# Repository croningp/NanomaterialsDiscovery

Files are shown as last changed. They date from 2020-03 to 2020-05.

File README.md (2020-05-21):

# Nanomaterials Discovery

Software for the paper "A Nanomaterials Discovery Robot for the Darwinian Evolution of Shape Programmable Gold Nanoparticles" as published in Nature Communications.



# Software Requirements

This software requires the following:
* Python >= 3.6 ([Linux](http://docs.python-guide.org/en/latest/starting/install3/linux/) / [Windows](https://www.python.org/downloads/release/python-363/))
* [Arduino IDE](https://www.arduino.cc/en/Main/Software)
* [Arduino Command Handler](https://github.com/croningp/Arduino-CommandHandler)
* [Arduino Command Tools](https://github.com/croningp/Arduino-CommandTools)

## Python Libraries

To install all rquired Python libraries, run the following command: `pip install -r requirements.txt`

# Running The System

Information on firmware setup can be found [here](#arduino-firmware-setup)

The majority of the execution paramters for this platform are all defined in the platform's [`info.json`](nanobot_run/info.json) file. This defined how many generations of experiments to perform as well as which pumps to use, what parameters to use for the GA etc.

## Initial Start
* Make appropriate changes to the `info.json` file
* Navigate to `nanobot_analysis`
* Run the `heimddall.py` file
  * This will create the appropriate folders and populate them depending on algorithm type
  * Leave this window running if using `GA` mode

## Execution
* Navigate to `nanobot_run`
* Run either the `experiment.py` or `ga_experiment.py` file depending on your experiment mode
  * This will look in the appropriate filepaths set up by the `heimdall.py` script and begin to load and execute experiments
* Leave this to run and process experiments
  * `heimdall.py` will automatically process and store experimental data in the appropriate locations
  * This wil lalso update the GA algorithm with fitness values as the generations proceed.
* Once the generations are finished, the experiment has concluded.

# Arduino Firmware Setup

The following is a description of how to set up the Arduino firmware for use with Commanduino.

## Installation
Clone the following repositories and follow the basic set up instructions within (Works with Windows/Linux)
* [Arduino Command Handler](https://github.com/croningp/Arduino-CommandHandler)
* [Arduino Command Tools](https://github.com/croningp/Arduino-CommandTools)

## Basic Setup

* Include the Command Handler and Command Manager at the top of your file and create a CommandManager instance

```C++
#include <CommandHandler.h>
#include <CommandManager.h>
CommandManager cmdMgr;
```

* Include the basic Arduino devices you will be using e.g. AccelSteppers, Servos, etc.

```C++
#include <AccelStepper.h>
#include <LinearAccelStepperActuator.h>

/* Additional Modules if necessary */
```

* Next, include the "Command" version of all your included devices from above

```C++
#include <CommandAccelStepper.h>
#include <CommandLinearAccelStepperActuator.h>
```

* Now instantiate the Arduino device objects and their Command equivalents
    * Note: The numbers are pins and these may change depending on your setup  

```C++
AccelStepper stepper1(AccelStepper::DRIVER, 54, 55);
CommandLinearAccelStepperActuator cmdStepper(stepper1, 3, 38);

/* Additional Object creation */
```

## Setup Function

Within the setup function, we use the created CommandDevice objects and add them to the manager. Each object is given a unique ID that the user specifies.

```C++
void setup() {
    /* Here, "drive_wheel" is the unique ID */
    cmdStepper.registerToCommandManager(cmdMgr, "drive_wheel");

    /* Register the remaining devices in a similar fashion */
}
```

## Loop Function

The loop function only contains single call for the manager to update. Nothing else is required here.

```C++
void loop() {
    cmdMgr.update();
}
```

# Pin Mappings

One of the most common uses of Commanduino is controlling stepper motors for movement, pumps, etc. To be able to use multiple stepper motors on a single Arduino board, a RAMPS shield is used, giving access to 5 possible motor locations and a collection of pins for other devices. Below is a list of pin mappings for using multiple stepper motors on a single RAMPS shield.

```C++
X_STEP_PIN         54
X_DIR_PIN          55
X_ENABLE_PIN       38

Y_STEP_PIN         60
Y_DIR_PIN          61
Y_ENABLE_PIN       56

Z_STEP_PIN         46
Z_DIR_PIN          48
Z_ENABLE_PIN       62

E0_STEP_PIN         26
E0_DIR_PIN          28
E0_ENABLE_PIN       24

E1_STEP_PIN         36
E1_DIR_PIN          34
E1_ENABLE_PIN       30

X_MIN_PIN          3
X_MAX_PIN          2
Y_MIN_PIN          14
Y_MAX_PIN          15
Z_MIN_PIN          18
Z_MAX_PIN          19
```

# Commanduino Setup

This platform uses the COmmanduino library to facilitate all communication between the Arduino board and our Python interface.
More examples can be found [here](https://github.com/croningp/commanduino/tree/master/examples/commanddevices).

## Configuration File

Example config file:

```json
{
    "ios": [
        {
            "port": "/dev/ttyACM0"
        },
        {
            "port": "/dev/ttyACM1"
        },
        {
            "port": "/dev/ttyACM2"
        }
    ],
    "devices": {
        "wheel": {
            "command_id": "wheel",
            "config": {
                "reverted_switch": true,
                "revereted_driection": true,
                "enabled_acceleration": false,
                "speed": 12000,
                "homing_speed": 12000,
                "acceleration": 2000
            }
        },
        "module1": {
            "command_id": "modY",
            "config": {
                "add_whats_necessary_for_device": true
            }
        },
        ...

    }
}
```

### IOS

The ```ios``` key represents the USB port the Arduino port is connected to. Commanduino will scan these ports to find the appropriate Arduino attached. For a single arduino attached, the above setup for ```ios``` is sufficient but for multiple Arduinos, it is best to assign them to a single port only. This prevents clashes.  
For port names:

* Linux
    * `"/dev/ttyACM{number}"`
* Windows
    * `"COM{number}"`

### Devices

The ```devices``` key holds all the information for the devices attached to the Arduino board. In the example above, ```wheel``` and ```module1``` are the names Commanduino will use to access them. Inside the devices, we have the ```command_id``` and ```config```.
* ```command_id```
    * This is unique ID given in the Arduino file. (See [Arduino Setup](#arduino-setup))
* ```config```
    * Dependent on the device type. (See [Commanduino Device Examples](https://github.com/croningp/commanduino/tree/master/examples/commanddevices))

## Commanduino File

Example Commanduino file:

```python
import os
import sys
import json
import time
import inspect

from commanduino import CommandManager # <-- Important!

class CoreDevice(object):
    """
    Class representing a core Commanduino system.
    Allows access to the modules attached

    Args:
        config (str): path to the Commanduino config file
    """
    def __init__(self, config):
        self.mgr = CommandManager.from_configfile(config) # Creates the CommandManager with JSON configuration file

        # Can now access devices attached e.g.
        self.wheel = self.mgr.wheel
        self.module1 = self.mgr.module1
        # etc. etc.

    ...

```

# Authors

* Daniel Salley
* Graham Keenan
* Abhishek Sharma
* Jonathan Grizou
* Sergio Martin Marti
* Leroy Cronin

All software and designs were developed as members of the [Cronin Group (University of Glasgow)](http://www.chem.gla.ac.uk/cronin/)

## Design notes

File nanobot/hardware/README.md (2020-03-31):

# NanoBot_hardware_V1
This repository contains all of the STL and DXF files and commercial component links needed to build an original 15 slot NanoBot platform

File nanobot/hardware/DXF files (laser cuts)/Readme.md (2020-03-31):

# DXF for laser cutting

The DXF file here contains the four laser cut acrylic parts (4mm) needed for the platform:
* The vial tray top and bottom
* The base plate
* The stirring ring on which the fans are mounted

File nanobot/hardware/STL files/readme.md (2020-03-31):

# Notes of these parts:

* These components have been designed for printing on an Objet series Connex 3D printer. This printer is extremely accurate meaning the allowances left between screw housings, part to part contact points etc. are in the order of microns. This means most (if not all) FDM print technology would be insufficient to print these parts as they currently stand. The structural parts (base and column etc) with a sufficient quality FDM printer may work with some manual adjustment after printing. However the drive and drive wheel relations are where the main issues will arise. This problem can be accounted for by the following steps:
  - Using the following links to [Geneva wheel basics](https://newgottland.com/2012/01/08/make-geneva-wheels-of-any-size/) and a [Genever wheel calculator](http://benbrandt22.github.io/genevaGen/) you may generate new dimensions needed for a fresh design with allowances sufficient for FDM printing.
  - Using the dimensions for the drive and drive wheel overall sizes provided in the DXF file included in this repo a replacement could be produced.

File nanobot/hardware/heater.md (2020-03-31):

## controller

- https://www.amazon.co.uk/Inkbird-Temperature-Controller-Thermostat-Thermocouple/dp/B00ADEGW3C/ref=sr_1_1?ie=UTF8&qid=1468329202&sr=8-1&keywords=ITC-100RL

## sensors

- http://uk.rs-online.com/web/p/thermocouples/8722503/

## heater

- http://incubatorwarehouse.com/incukit-xl.html

- heater from this company to heat the chamber: http://kuehlingkuehling.de/product-category/3d-printers/

## various

- http://uk.rs-online.com/web/p/non-latching-relays/7826969/

- http://uk.rs-online.com/web/p/non-latching-relays/0351572/

- http://uk.rs-online.com/web/p/crimp-terminal-boots/7454794/

- http://uk.rs-online.com/web/p/crimp-receptacles/0534351/?origin=null|fp&cm_sp=featureproducts-_-FeaturedProductsContent-_-0534351

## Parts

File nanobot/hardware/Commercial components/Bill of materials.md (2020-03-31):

# Bill of Materials

This page contains a brief description of and links for the commercially available parts needed to produce this platform   

# Wheel platform

* Structural: V-slot aluminium [profile](http://ooznest.co.uk/V-Slot/Linear-Rails/V-Slot-Linear-Rail-2020mm):
  - 290mm x 2
  - 300mm x 2
  - 260mm x 1
  - 120mm x 2
  - 180mm x 1
* Structural: M5 x 12, 8 and 6mm [screws](http://ooznest.co.uk/Low-Profile-M5-Bolts?search=M5) with accompanying [drop-in tee nuts](http://ooznest.co.uk/Drop-In-Tee-Nuts?search=drop)
* Structural: Universal (single) L-[bracket](http://ooznest.co.uk/V-Slot/Brackets/Universal-L-Brackets)
* Structural: 2-hole [joining plate](http://ooznest.co.uk/V-Slot/Brackets/2-Hole-Joining-Plate) x 2
* Structural: [Acrylic](http://www.acrylic-online.co.uk/) sheet 4mm (600 x 500mm minimum) x 1
* Structural: Assorted 3D printed [parts](https://github.com/croningp/NanoBot_hardware_V1/tree/master/STL%20files)
* Structural: Assorted M3 x 12/16/20/30mm [screws](https://www.accu.co.uk/en/64-low-head-cap-screws#elasticsearch_id_feature_655793=655793_697&elasticsearch_id_feature_655794=655794_1&id_elasticsearch_category=64&orderby=ranking&orderway=asc)
* Electronic: Arduino mega 2560 and [RAMPS](http://ooznest.co.uk/RAMPS-14-Controller-Board-Premium?search=ramps) 1.4 with 2 DRV8825. The options for the Arduino and stepper motor drivers are included in the drop down menu options x 1
* Electronic: 25 x 25 x 10 mm DC [fans](http://ooznest.co.uk/12V-DC-25mm-Fan?search=25mm) for the stirring array x 15
* Electronic: Corsair SF450 [power supply](https://www.amazon.co.uk/Corsair-SF450-Fully-Modular-Supply/dp/B01CR5XJR6) x 1
* Electronic: Nema17 stepper x 1 [motor](https://www.accu.co.uk/en/nema-17-stepper-motors/496466-NEMA17-40-1-7-1-8?uk_google_shopping=1&c=3&mkwid=s_dc&pcrid=209417175255&kword=&match=&plid=&gclid=CjwKCAjwyrvaBRACEiwAcyuzRABbU2tFQi1yQNd7_wL3WTq4IH_Au6toDr7JEU6PAY236qg2CjXwfBoCHX8QAvD_BwE) with accompanying Pololu aluminium mounting [hub](https://www.pololu.com/product/1998) (this part joins the drive wheel to the stepper motor shaft) x1
* Electronic: Any 2 and 4 way crimp housings. It matters that the crimps match the plastic housings you chose, beyond that many types can be used.
* Electronic: Stepper motor to RAMP connection [housings](https://uk.rs-online.com/web/p/products/2964956/?grossPrice=Y&cm_mmc=UK-PLA-DS3A-_-google-_-PLA_UK_EN_Connectors-_-Pcb_Connectors%7CPcb_Connector_Housings-_-PRODUCT+GROUP&matchtype=&gclid=CjwKCAjwyrvaBRACEiwAcyuzROPybPC5snwsWROQbjWMcLjBqjNpqaopkuRLn16-PZd7FsV7mNAtghoCZcMQAvD_BwE&gclsrc=aw.ds) x 1 per stepper motor (use with appropriate crimps for this housing)
* Electronic: End stop switch (modular syringe driver) crimp housings for RAMPS [connection](https://www.molex.com/molex/products/datasheet.jsp?part=active/0050579003_CRIMP_HOUSINGS.xml) (use with appropriate crimps for this housing)
* Pumps: Tricontinent [c-series pumps](https://www.tricontinent.com/c-series-syringe-pumps.html) x 8
* Pumps: Tubing and connectors from Kinesis/Cole-Palmer:
  - [1.6mm](https://kinesis.co.uk/tubing-tubing-ptfe-1-16-1-6mm-od-x-0-8mm-id-20m-008t16-080-20.html) OD tubing
  - [3.2mm](https://kinesis.co.uk/tubing-tubing-ptfe-1-8-3-2mm-od-x-1-5mm-id-10m-008t32-150-10.html) OD tubing
  - IDEX flangeless fittings Nat PP [1/16in](https://www.idex-hs.com/store/fluidics/fluidic-connections/fittings/flat-bottom-fittings/flangeless-fittings/flangeless-fitting-natural-polypropylene-1-4-28-flat-bottom-for-1-16-od.html)
  - IDEX flangeless fittings Nat PP [1/8](https://www.idex-hs.com/store/fluidics/fluidic-connections/fittings/flat-bottom-fittings/flangeless-fitting-natural-polypropylene-1-4-28-flat-bottom-for-1-8-od.html)
  - Restek Thames 1/4-28 female to male [Luer]() asy
  - Adhesive Dispensing (AD5125TLC) 25 gauge TLC lined tip [needle]()
* Fan stirring [magnets](https://www.first4magnets.com/rectangular-magnets-c35/15-x-4-x-4mm-thick-n42-neodymium-magnet-2-2kg-pull-p3499#ps_1-789) x 30
* Driven wheel [bearing](https://uk.rs-online.com/web/p/ball-bearings/4420082/) x 1
* Modular syringe [driver] (https://github.com/croningp/ModularSyringeDriver)

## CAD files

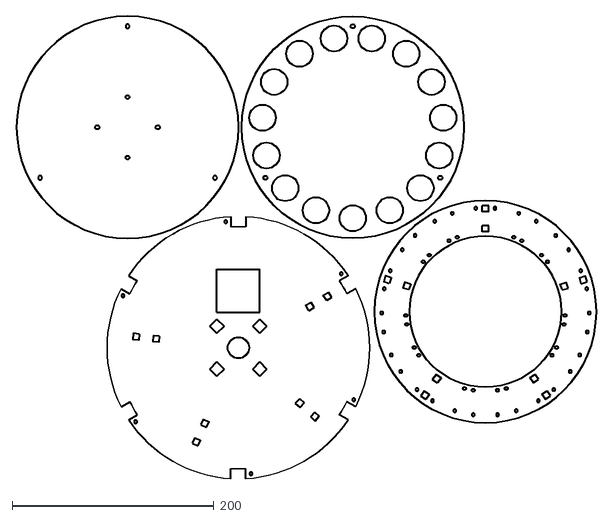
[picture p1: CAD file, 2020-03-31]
nanobot/hardware/DXF files (laser cuts)/NanoBot_cuts.dxf
574.4 x 458.0

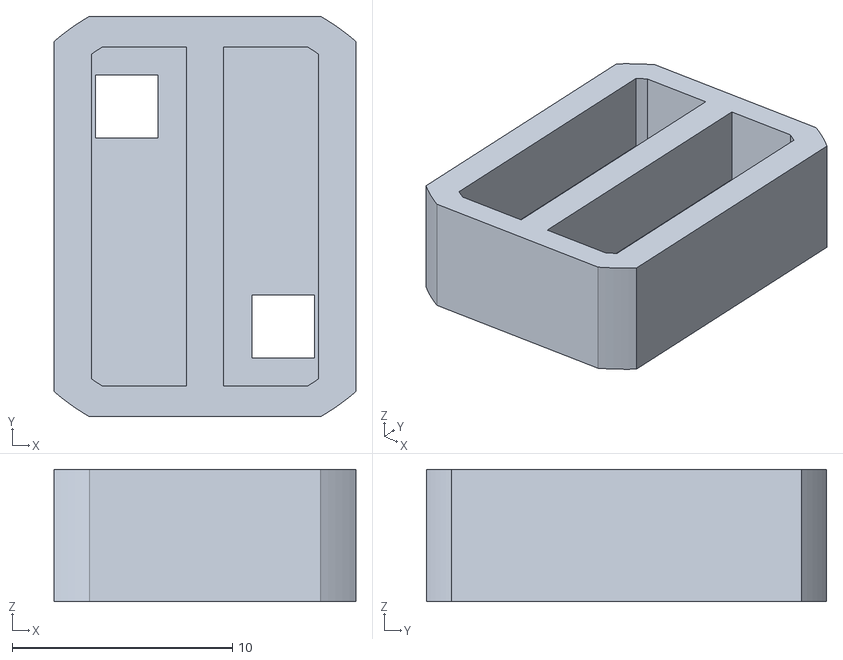
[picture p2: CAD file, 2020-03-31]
nanobot/hardware/STL files/NanoBot magnet housing 2.2kg pull rectangular.stl
13.7 x 18.2 x 6.00

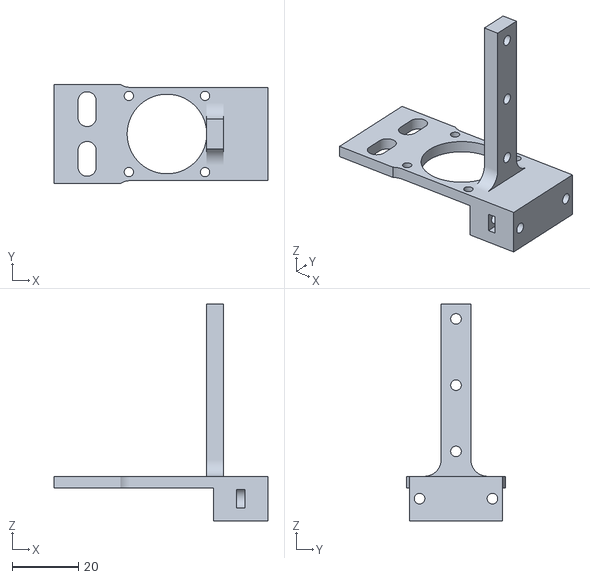
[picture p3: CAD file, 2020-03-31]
nanobot/hardware/STL files/Syringe driver prints/NanoBot syringe body.stl
64.6 x 30.0 x 65.5

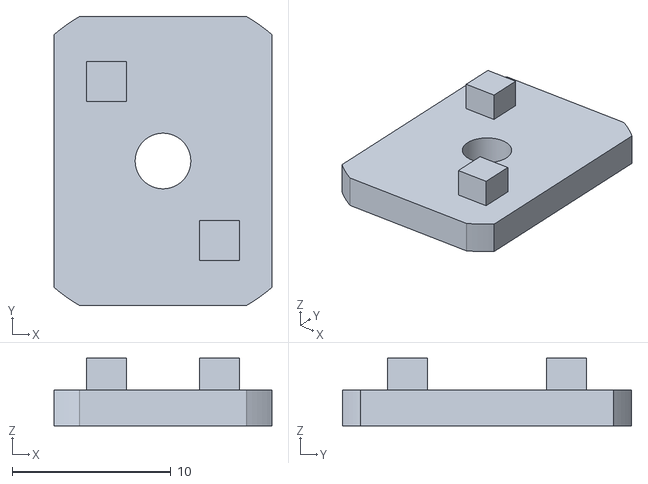
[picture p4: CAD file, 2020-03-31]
nanobot/hardware/STL files/NanoBot magnet housing base.stl
13.7 x 18.2 x 4.25

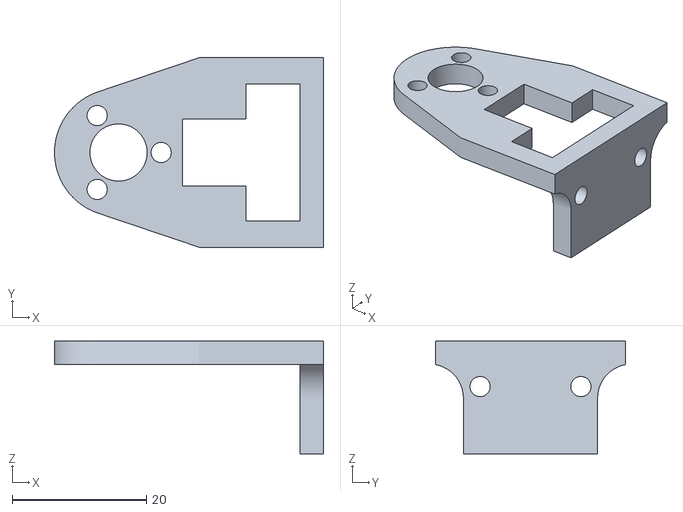
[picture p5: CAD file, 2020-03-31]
nanobot/hardware/STL files/Syringe driver prints/NanoBot syringe carriage body.stl
40.0 x 28.2 x 16.8

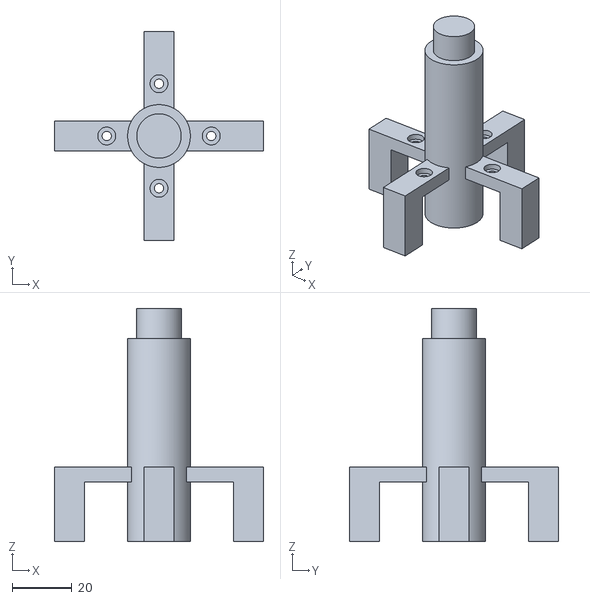
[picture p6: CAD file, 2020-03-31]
nanobot/hardware/STL files/NanoBot Column mount.stl
70.0 x 70.0 x 78.0

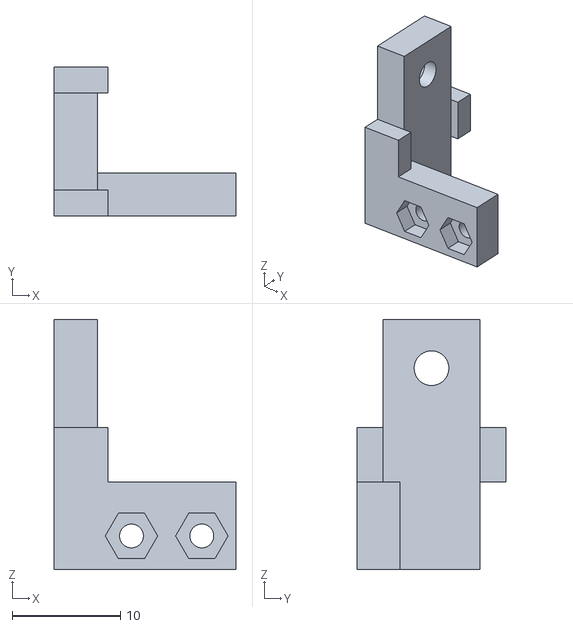
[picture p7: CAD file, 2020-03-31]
nanobot/hardware/STL files/Syringe driver prints/NanoBot syringe end stop switch mount.stl
16.8 x 13.8 x 23.1

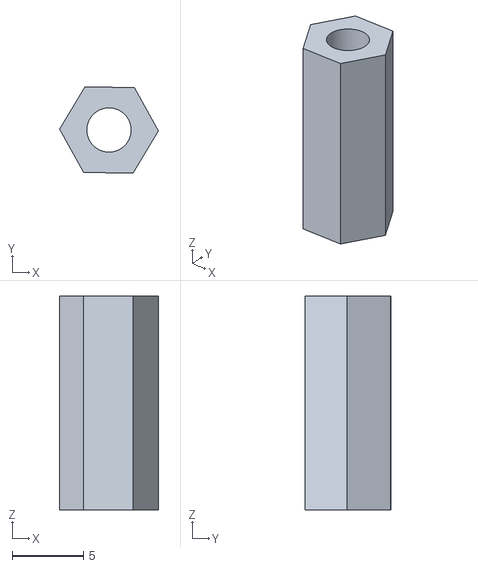
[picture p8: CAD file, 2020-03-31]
nanobot/hardware/STL files/NanoBot vial tray hex spacer.stl
6.93 x 6.06 x 15.0

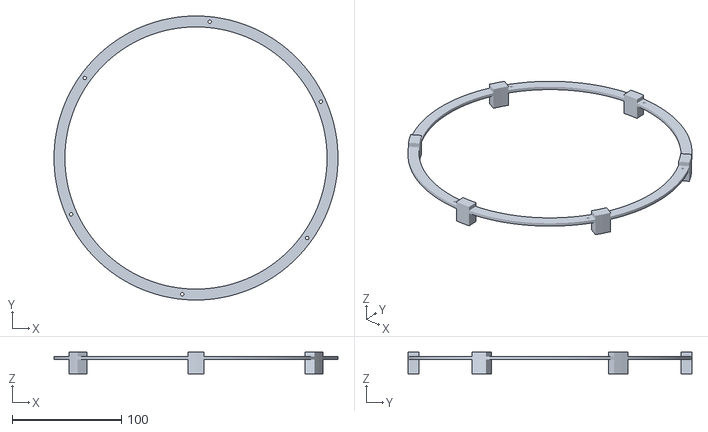
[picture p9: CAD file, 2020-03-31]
nanobot/hardware/STL files/NanoBot Base platform.stl
260.0 x 260.0 x 20.0

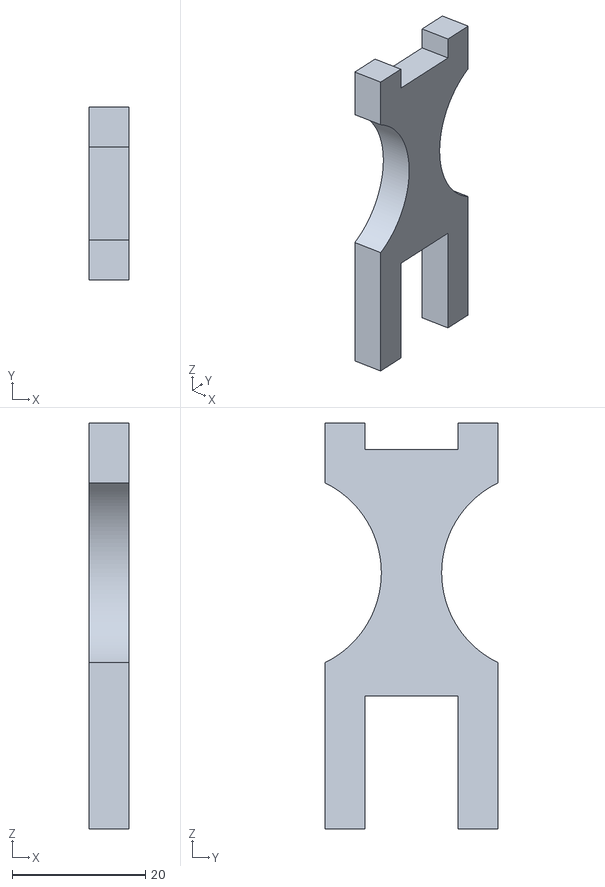
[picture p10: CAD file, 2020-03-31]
nanobot/hardware/STL files/NanoBot Stir ring support.stl
6.00 x 26.0 x 61.0

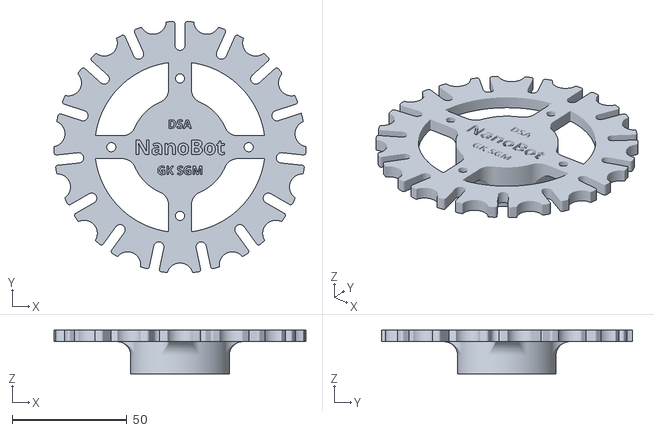
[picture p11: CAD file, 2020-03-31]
nanobot/hardware/STL files/NanoBot Driven wheel.stl
110.0 x 109.6 x 19.0

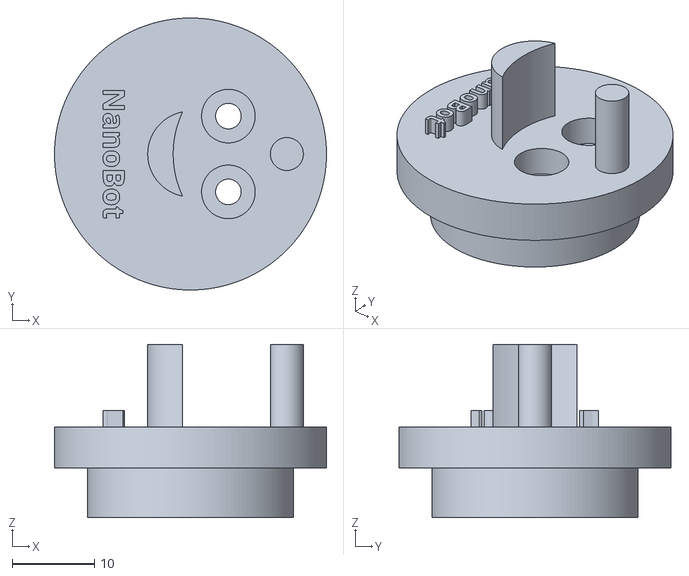
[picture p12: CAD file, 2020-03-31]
nanobot/hardware/STL files/NanoBot Drive wheel.stl
33.0 x 33.0 x 21.0

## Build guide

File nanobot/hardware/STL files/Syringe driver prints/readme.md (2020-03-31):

# Modular syringe driver:

This set of STL files are an in house design for a Modular syringe driver capable of Z-motion movement that allows us to lower probes, tubing etc. into our reaction vials.  
The links for the custom made stepper motor and the other commercial hardware needed to make this unit can be found in the 'commercial parts' folder

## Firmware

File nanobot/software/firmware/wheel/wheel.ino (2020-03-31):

/**
#define X_STEP_PIN         54
#define X_DIR_PIN          55
#define X_ENABLE_PIN       38

#define Y_STEP_PIN         60
#define Y_DIR_PIN          61
#define Y_ENABLE_PIN       56

#define Z_STEP_PIN         46
#define Z_DIR_PIN          48
#define Z_ENABLE_PIN       62

#define E0_STEP_PIN         26
#define E0_DIR_PIN          28
#define E0_ENABLE_PIN       24

#define E1_STEP_PIN         36
#define E1_DIR_PIN          34
#define E1_ENABLE_PIN       30

 #define X_MIN_PIN          3
 #define X_MAX_PIN          2
 #define Y_MIN_PIN          14
 #define Y_MAX_PIN          15
 #define Z_MIN_PIN          18
 #define Z_MAX_PIN          19
 **/

#include <CommandHandler.h>
#include <CommandManager.h>
CommandManager cmdMgr;

/* Include the base files needed such as Accel Stepper, Servo etc */
#include <AccelStepper.h>
#include <LinearAccelStepperActuator.h>

/* Include the "Command" version of the above */
#include <CommandAccelStepper.h>
#include <CommandLinearAccelStepperActuator.h>

//PWM for fans
#include <CommandAnalogWrite.h>

// Laser Power Control
#include <CommandDigitalWrite.h>


/* Set up the base objects and Command objects */
AccelStepper stepperX(AccelStepper::DRIVER, 54, 55);
CommandLinearAccelStepperActuator X(stepperX, 3, 38);

AccelStepper stepperY(AccelStepper::DRIVER, 60, 61);
CommandLinearAccelStepperActuator Y(stepperY, 14, 56);

AccelStepper stepperZ(AccelStepper::DRIVER, 46, 48);
CommandLinearAccelStepperActuator Z(stepperZ, 18, 62);

AccelStepper stepperE0(AccelStepper::DRIVER, 26, 28);
CommandLinearAccelStepperActuator E0(stepperE0, 2, 24);

AccelStepper stepperE1(AccelStepper::DRIVER, 36, 34);
CommandLinearAccelStepperActuator E1(stepperE1, 15, 30);


//PWM
CommandAnalogWrite ring(8);
CommandAnalogWrite laser(4);


/* Do this for the rest of your devices */

void setup() {
    Serial.begin(115200); // Always 115200

    /* Register devices to the command manager */
    X.registerToCommandManager(cmdMgr, "wheel"); 
    Y.registerToCommandManager(cmdMgr, "zdsd");
    Z.registerToCommandManager(cmdMgr, "sdsd");
    E0.registerToCommandManager(cmdMgr, "msd1"); 
    E1.registerToCommandManager(cmdMgr, "pumpE1");
    
    /* Do this for the rest of your devices */
    ring.registerToCommandManager(cmdMgr, "ring");
    laser.registerToCommandManager(cmdMgr, "laser");

    cmdMgr.init();
}

void loop() {
    cmdMgr.update();
    /* Nothing else needed here */
}
